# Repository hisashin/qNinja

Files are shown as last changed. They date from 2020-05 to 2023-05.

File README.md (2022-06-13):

# Open Source $300 Real Time PCR and LAMP machine "qNinja"

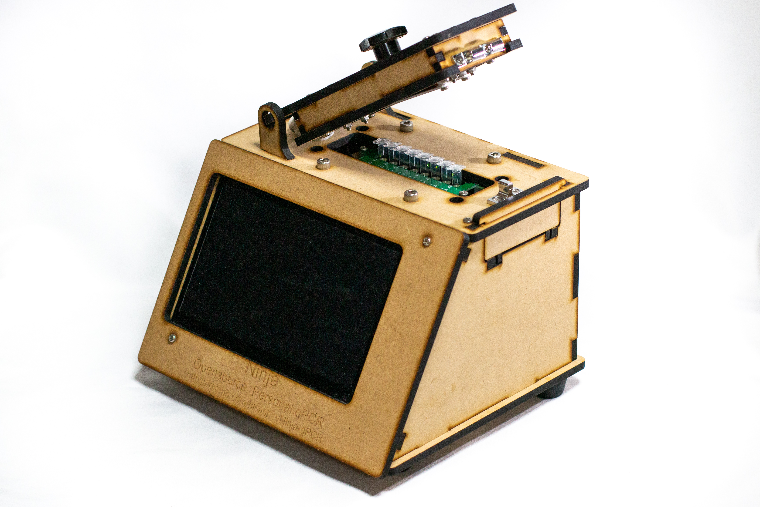
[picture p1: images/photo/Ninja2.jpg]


# $50 qLAMP machine "[qNinja Lite](https://github.com/hisashin/qNinjaLite)" is also available



## Reference Links
- [qNinja portal](https://qninja.hisa.dev)

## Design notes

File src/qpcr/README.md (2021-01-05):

# Ninja-qPCR core application

This directory contain the core application of Ninja-qPCR.

* ninjaqpcr.js : Core functionalities for running experiments and control devices. [More...](./API_ninjaqpcr.md)
* experiment_manager.js : Manager of experiment logs [More...](./API_log_manager.md)
* protocol_manager.js : Manager of experiment logs [More...](./API_protocol_manager.md)
* optics_analysis.js : Fluorescence analyzer class providing mathematical functionalities
  * Basic qPCR analysis
  * Baseline & threshold calculation (users can also set these values manually.)
  * Standard curve
  * Melt curve analysis

## Standalone demo

"demo.js" shows a demo of calling the core module. It simulates a typical qPCR + melt curve profile.

```
node demo.js
```

## Usage of NinjaQPCR class
Import the qPCR module.

```
const NinjaQPCR = require("./ninjaqpcr");
const hardwareConf = require("./conf/dummy_hardware_conf.js");
const qpcr = new NinjaQPCR(hardwareConf);

```

## Protocols

### Examples

* protocol_example.js : Typical protocol with initial hold, qPCR cycles and melt curve.
* protocol_example.js : Very short protocol for rapid testing.

### Format

```
{
  id: "2B93DB54-E14D-444F-BAEE-5B595F3FB917",
  lid_temp: 40.0,
  final_hold_temp:20.0,
  name: "Dev Protocol",
  stages: [
    {  
      type: Constants.StageType.HOLD,
      repeat: 1,
      steps: [
        { label:"hold", temp:DEMO_TEMP_HIGH, duration:5.0, data_collection:[] }
      ]
    },
    {
      type: Constants.StageType.QPCR,
      repeat: 3,
      steps: [
        { label:"denature", temp:DEMO_TEMP_HIGH, duration:6.0, data_collection:[3, 4] },
        { label:"anneal", temp:DEMO_TEMP_MEDIUM, duration:6.0, data_collection:[3, 4] },
        { label:"extend", temp:DEMO_TEMP_LOW, duration:6.0, data_collection:[3, 4] }
      ]
    },
    {
      type: Constants.StageType.MELT_CURVE,
      repeat: 1,
      steps: [
        { label:"denature", duration:5, temp:DEMO_TEMP_HIGH, data_collection:[] },
        { label:"cool", duration:5, temp:DEMO_TEMP_MEDIUM, data_collection:[] },
        { label:"melt", ramp_speed: 0.4, duration:5.0, temp:DEMO_TEMP_HIGH, data_collection:[1] }
      ]
    }
  ]
};
```

### Fields

Protocol
* id : UUID of the protocol. It corresponds the name of the file.
* lid_temp : Temperature of the head lid (in Celsius)
* final_hold_temp : Temperature of the head lid (in Celsius)
* name : Name of the protocol
* stages : List of stages (See below.)

Stage
* type : Type of the stage. 1=HOLD, 2=QPCR, 3=MELT_CURVE, 4=PCR (without fluorescence measurement)
* repeat : Number of cycles
* steps : List of steps (See below.)

Step
* label : Name
* duration : Hold duration (in secs)
* temp : Well temperature (in Celsius)
* data_collection : List of fluorescence data collection. 1=RAMP_CONTINUOUS, 2=HOLD_CONTINUOUS, 3=RAMP_END, 4=HOLD_END

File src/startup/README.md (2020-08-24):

Startup scripts

* The device is configured by /etc/rc.local to execute startup.sh.
* It checks the input value on the mode pin.
* If the mode pin's value is HIGH, it calls start_ap_mode.sh
* If the mode pin's value is LOW, it calls start_normal_mode.sh

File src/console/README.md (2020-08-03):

# Ninja qPCR Console

## Server

```
node ws_server.js
```

The server runs on localhost:2222.

The server app has WebSocket and REST interfaces. 

While the WebSocket API provides real-time device monitor and controller functionalities, the REST API is intended to manage protocols and logs. 
Exceptionally, paths beginning with "/device" return information about ongoing experiments so that a browser can show the progress just after joining it.

### REST API:

* /protocols : 
  * GET: Get list of protocols
  * POST: Add new protocol
* /protocols/{protocol_id} : 
  * GET: Get single protocol
  * PUT: Update single protocol
  * DELETE: Delete single protocol
* /logs : Get list of experiment logs
* /logs/latest : Get latest log
* /logs/{log_id} : Get single log
* /device : Get device status
* /device/experiment : Get current experiment
* /device/experiment/protocol : Get current protocol (Empty if the device is idle)
* /device/experiment/config : Get current protocol (Empty if the device is idle)
* /device/experiment/progress : Get progress of current protocol
* /device/experiment/baseline" : Get fluorescence baseline & threshold values

### WebSocket API:

#### Client to server commands
```
{
  category: <String>,
  data: <Object>
}
```

Categories

* experiment.start :  Start an experiment
* experiment.pause : Pause an ongoing experiment
* experiment.resume : Resume an paused experiment
* experiment.abort : Abort an ongoing or paused experiment
* experiment.finish : Finish the experiment. This command is accepted only when the device is at "Final hold" state after an experiment. By this command, the device stop heat units and become "Idle" again.
* experiment.registerProtocol : Register a protocol for the next experiment.

#### Server to client

```
{
  category: <String>,
  data: <Object>
}
```
* experiment.transition : Experiment-level status changes such as stages, cycles and steps.
* experiment.progress : Current progress including temperatures, stages and steps. The latest data can also be obtained by /device/progress of the REST API.
* experiment.fluorescence : Results of fluorescence measurements.
* experiment.fluorescenceEvent : Significant events related to fluorescence measurements, such as 
  * Start and end of continuous measurement
  * Notification of baseline and threshold determination.
* experiment.start
* experiment.finish
* device.transition : Notify device-level (not experiment-level) status change
* (TODO) device.error : Notify device-level errors

Each category corresponds to event handlers of NinjaQPCR class:

| Category | Function |
| ---- | --- |
| experiment.transition | onThermalTransition |
| experiment.progress | onProgress |
| experiment.fluorescence | onFluorescenceDataUpdate |
| experiment.fluorescenceEvent | onFluorescenceEvent |
| experiment.start | onStart |
| experiment.finish | onComplete |
| device.transition | onDeviceStateChange |
| device.error | onError |

For details of data format, see [the document of NinjaQPCR class](../qpcr/API_ninjaqpcr.md).

# Client

The client is implemented as a Vue.js app.

Run (and hot reload):
```
npm run serve
```
By default, the app runs on
- Local:   http://localhost:8080 
- Network: http://192.168.1.15:8080

Build for production:
```
npm run build
```

Static files (HTML, css and js) are saved to "dist" directory.

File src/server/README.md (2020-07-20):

# Ninja-qPCR server

The endpoint for the console that controls the instrument.

It should handle the following functions:

* Start, pause and experiment experiments (experiment protocol)
* Return current status of the thermal cycler
* Return fluorescence data
* Notify thermal cycler's transition events (stages and steps)
* Notify errors and alerts

## Development
```
yarn
yarn start
```

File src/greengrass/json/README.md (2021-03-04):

# Test your POST_URL

```
curl -X POST -H "Content-Type: application/json" -d @src/greengrass/json/qPCR-protocol-sample.json (POST_URL)
curl -X POST -H "Content-Type: application/json" -d @src/greengrass/json/qPCR-log-sample.json (POST_URL)
```

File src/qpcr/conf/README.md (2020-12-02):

This directory contain hardware config files.

* hardware.json : Top config including well layout, model specifications.
* ninjaqpcr_*.js : Board-specific files. Some files are intended to run only with some parts of the device or only simulator.

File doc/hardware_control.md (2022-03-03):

# Fluorescence measurement

## Sequence

1. Activate LED
    * Set potentiometer value
    * Select LED channel
2. Select photodiode MUX channel
    * Select MUX
    * Select channel
3. Read ADC value 
    * Wait until the ADC value becomes stable
    * Read ADC value

This sequence is performed for each channel.

# Wiring

* All I2C devices on the board share SDA and SCL wires.
* Device addresses
    * Potentiometer (For LED control) : 0x2F
    * LED driver : 0x05
    * ADC : 0x40
* Photodiodes
    * Wells and MUX channels association
        * North (Ch 0) (Well 1 - Well 8) 7,5,3,1,15,13,11,9
        * North (Ch 1) (Well 1 - Well 8) 6,4,2,0,14,12,10,8
        * South (Ch 0) (Well 9 - Well 16) 8,10,12,14,0,2,4,6
        * South (Ch 1) (Well 9 - Well 16) 9,11,13,15,1,3,5,7
* LED and driver channels association
    * North (Well 1 - Well 8) 11,10,9,8,12,13,14,15,
    * South (Well 9 - Well 16) 4,5,6,7,3,2,1,0
    
# Pseudo code

## Setup
```

pin_mux_select = ...
pin_mux_s0 = ...
pin_mux_s1 = ...
pin_mux_s2 = ...
pin_mux_s3 = ...

well_to_led_ch = [
    11,10,9,8,12,13,14,15,
    4,5,6,7,3,2,1,0
]

well_to_mux_ch = [
    [ 
        7,5,3,1,15,13,11,9, #  North
        8,10,12,14,0,2,4,6 # South
    ], # Optical channnel 0
    [
        6,4,2,0,14,12,10,8, #  North
        9,11,13,15,1,3,5,7 # South
    ] # Optical channnel 1
]

func setup () : 
    init_i2c_bus()
    led_driver_init()
    adc_init()
```

## Measure all Wells

```
for well in 0..15 :
    for optical_channel in 0..1 :
        fluo = read_fluo (well, optical_channel)

func read_fluo (well, optical_channel) :

    led_channel = well_to_led_ch[well]
    mux = (int) well / 8  # 0=>North, 1=>South
    mux_channel = well_to_mux_ch[optical_channel][well]

    set_potentiometer_wiper (pot_wiper)
    select_led_channel (led_channel)
    gpio_write (pin_mux_select, mux)
    select_mux_channel (mux_channel)
    adc_select_channel () # AIN3->P, AIN2->N
    delay_msec (2)
    fluo_raw = adc_read_conversion ()
    return calc_fluo (fluo_raw, pot_wiper)
```

## MUX
```
func select_mux_channel (channel) :
    gpio_write (pin_mux_s0, 0x01&(ch>>0) )
    gpio_write (pin_mux_s1, 0x01&(ch>>1) )
    gpio_write (pin_mux_s2, 0x01&(ch>>2) )
    gpio_write (pin_mux_s3, 0x01&(ch>>3) )

```
## LED driver
```
i2c_addr_led_driver = 0x05
REG_ADDR_LEDOUT0 = 0x02

func led_driver_init () :
    # Set blank control mode
    i2c_write(i2c_addr_led_driver, [0x00, 0b10001001] )

    first_val = 0x18 | (0b01 << 7)
    vals = [first_val]
    for 0..16
        vals.append(0xFF)
    # Send 17 bytes (address + 0xFF x 16)
    i2c_write(i2c_addr_led_driver, vals)

func select_led_channel (channel) :
    leds = [...]
    for i in 0..15
        leds[i] = (i == channel) ? 1 : 0

    vals = []

    # 4 bytes for 16 channels
    for group in 0..3
        # 2 bits for each channel
        val = 0b00000000
        for i in 0..3
            mode = leds[group * 4 + i]
            val = val | (mode << (i*2))
        vals[group] = val

    addr_byte = REG_ADDR_LEDOUT0 | (0b01 << 7)

    # Send 5 bytes (address + LED values)
    reg_values = [addr_byte] + [vals] 
    i2c_write(i2c_addr_led_driver, reg_values)

```
## Potentiometer
```
i2c_addr_pot = 0x2F

func set_potentiometer_wiper (wiper) : 
    val0 = wiper >> 8 & 0x01
    val1 = wiper & 0xFF
    i2c_write(i2c_addr_pot, [val0, val1]);

```

## ADC

```
i2c_addr_adc = 0x40

COMMAND_RDATA = 0x10
COMMAND_RREG = 0b00100000 # 0010 rrxx : Read register at address rr
COMMAND_WREG = 0b01000000
COMMAND_SSYNC = 0b00001000

func adc_write_reg (reg_address, value) :
    command = COMMAND_WREG | (0b11&reg_address) << 2;
    i2c_write(i2c_addr_adc, [command, value])
    i2c_send(i2c_addr_adc, COMMAND_SSYNC)

func adc_read_reg (address) :
    command = COMMAND_RREG | (0b11&addr) << 2;
    i2c_send(i2c_addr_adc, command)
    return i2c_receive(i2c_addr_adc)

func adc_init () :
    data_rate_600sps = 0b101
    current_conf_val = adc_read_reg(0x01);
    new_conf_val = (0b00011111 & current_conf_val) | (data_rate_600sps << 5)
    adc_write_reg(0x01, new_conf_val)

func adc_select_channel () :
    mux_bits = 0b0111 # AIN3->P, AIN2->N
    current_val = adc_read_reg(0x00)
    new_val = (0b00001111 & current_val) | (mux_bits << 4);
    adc_write_reg(0x00, new_val);

func adc_read_conversion () : 
    i2c_send(i2c_addr_adc, COMMAND_RDATA)

    # Read 3 bytes
    val = i2c_receive(i2c_addr_adc)
    val <<= 8;
    val |= i2c_receive(i2c_addr_adc)
    val <<= 8;
    val |= i2c_receive(i2c_addr_adc)

    if (val & 0x00800000)
      val = ~val + 1;
      val = -(val & 0xFFFFFF)
    return val / (1.0 * 0x00800000)

func calc_fluo (fluo_raw, pot_wiper) :
    # TODO

```

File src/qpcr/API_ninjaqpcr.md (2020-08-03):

# class NinjaQPCR

## constructor (hardwareConf)

## Public functions

### setEventReceiver (receiver)

Set an object to receive events.

### start (protocol)

### pause ()

### resume ()

### abort ()

### finish ()

## Event handling

You can get notified of events by setting a receiver object.

```
qpcr.setEventReceiver(receiver)
```

Functions below are defined. All of them are optional.
  
### onProgress(data)

Tells current progress of the experiment every 0.5 second.

```
{ 
  well: 50,
  lid: 40,
  state: 
  { 
    state: 'ramp', 
    stage: 0,
    repeat: 0,  
    step: 0, 
    stepElapsed: 5025 
  },
  remaining: 153475,
  elapsed: 8045 
}
```

* well (float) : Temperature of the well block
* lid (float) : Temperature of the heat lid
* remaining (long int) : Estimated remaining time in milliseconds
* elapsed (long int) : Elapsed time in milliseconds
* state (object) : State of the experiment
  * state (string) : Label of the state. (preheat/ramp/hold/complete)
  * stage (int) (*) : Index of the stage. 
  * repeat (int) (*) : Index of the cycle
  * step (int) (*) : Index of the step
  * stepElapsed (long) (*) : Elapsed time of the step in milliseconds
  
Fields with "(*)" are empty when the state is "preheat" or "compete".

### onThermalTransition(transition)

Notifies state changes of the thermal cycler.

```
{ 
  from:
   { state: 'hold', stage: 1, step: 0, repeat: 0, stepElapsed: 5028 },
  to:
   { state: 'ramp', stage: 1, step: 0, repeat: 0, stepElapsed: 0 } }
}
```

* from (object) : Previous state.
* to (object) : Current state.

### onError(error)

Notifies device errors.
  
### onStart(data)

Notifies that the experiment started.

```
{ 
  id: '34aa55dc-e63d-4562-836d-6900dee11608',
  protocol: '2B93DB54-E14D-444F-BAEE-5B595F3FB917' 
}
```
  
### onComplete(data)

Tell the end of the experiment. The well unit is still working to keep the final hold temperature.
"Finish" command is needed to completely stop heat units and make the device ready again.

```
{ 
  id: '34aa55dc-e63d-4562-836d-6900dee11608',
  protocol: '2B93DB54-E14D-444F-BAEE-5B595F3FB917' 
}
```
  
### onDeviceStateChange(data)
  
### onFluorescenceDataUpdate(data)

Tell result of fluorescence measurement.

```
[ 0.10801242489714052,
  0.12294936026411177,
  0.11420738944199534,
  0.13175764679533242,
  0.12903787941280465,
  0.10887617636084554,
  0.13071267983725746,
  0.12279237404504303 ]
```
  
### onFluorescenceEvent (data)

```
{ type: 'measure' }
```

* type (string) : Type of the event

Event types are

* measure : One-shot measurement (at ends of steps of qPCR stages)
* start : Starting continuous measurement (for baseline or melt curve)
* stop : Stopping continuous measurement
* baseline : End of baseline measurement. At this time, thresholds are determined automatically.

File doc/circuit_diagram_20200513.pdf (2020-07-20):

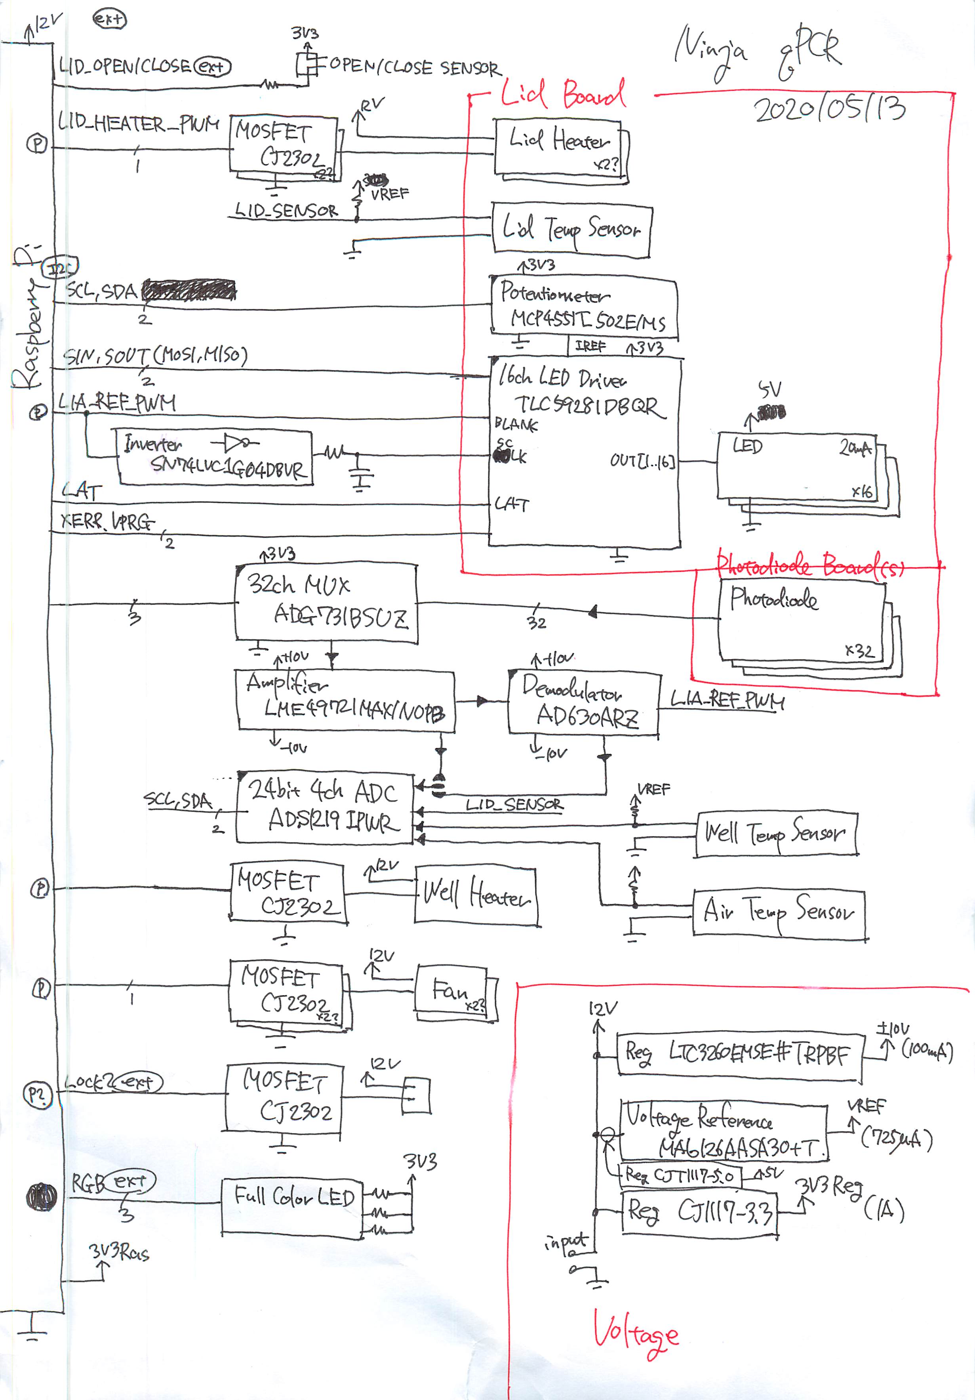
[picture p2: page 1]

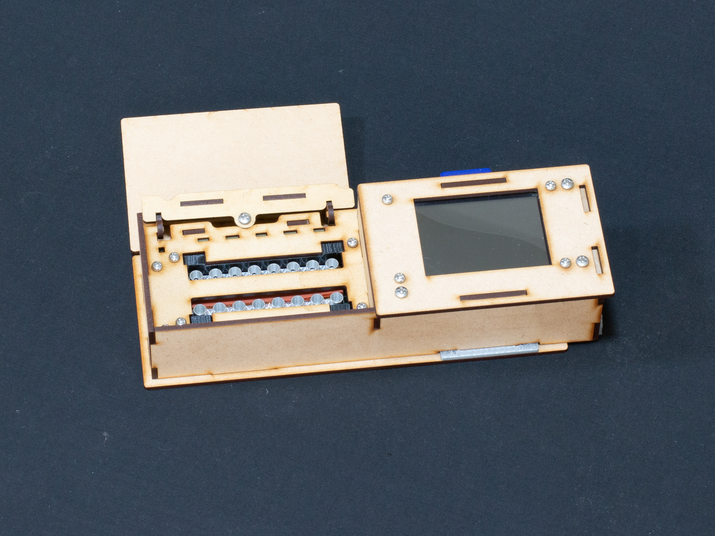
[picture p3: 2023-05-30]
images/photo/qlite_mdf_open_1.jpg

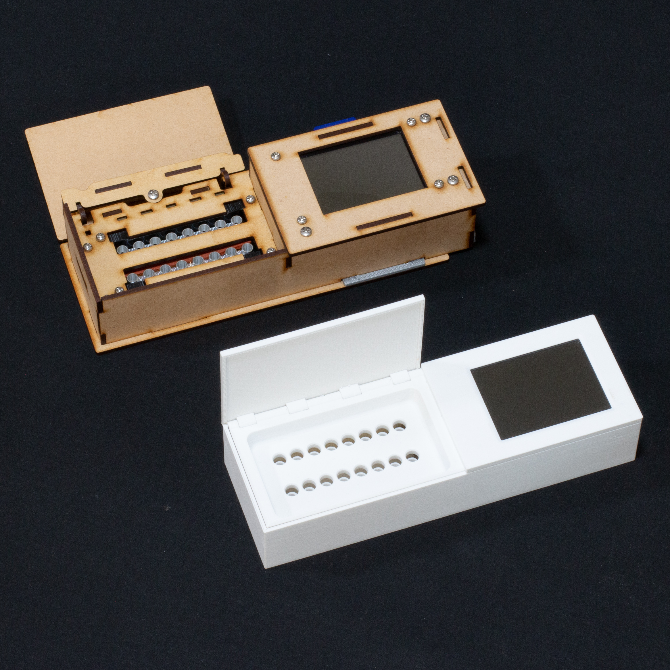
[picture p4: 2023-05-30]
images/photo/20230530/v_IMG_2483.jpg

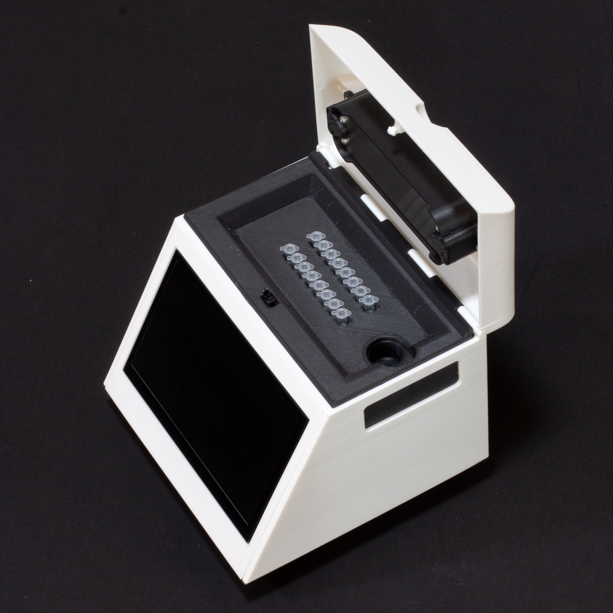
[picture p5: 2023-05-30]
images/photo/q_3dp_open_3.jpg

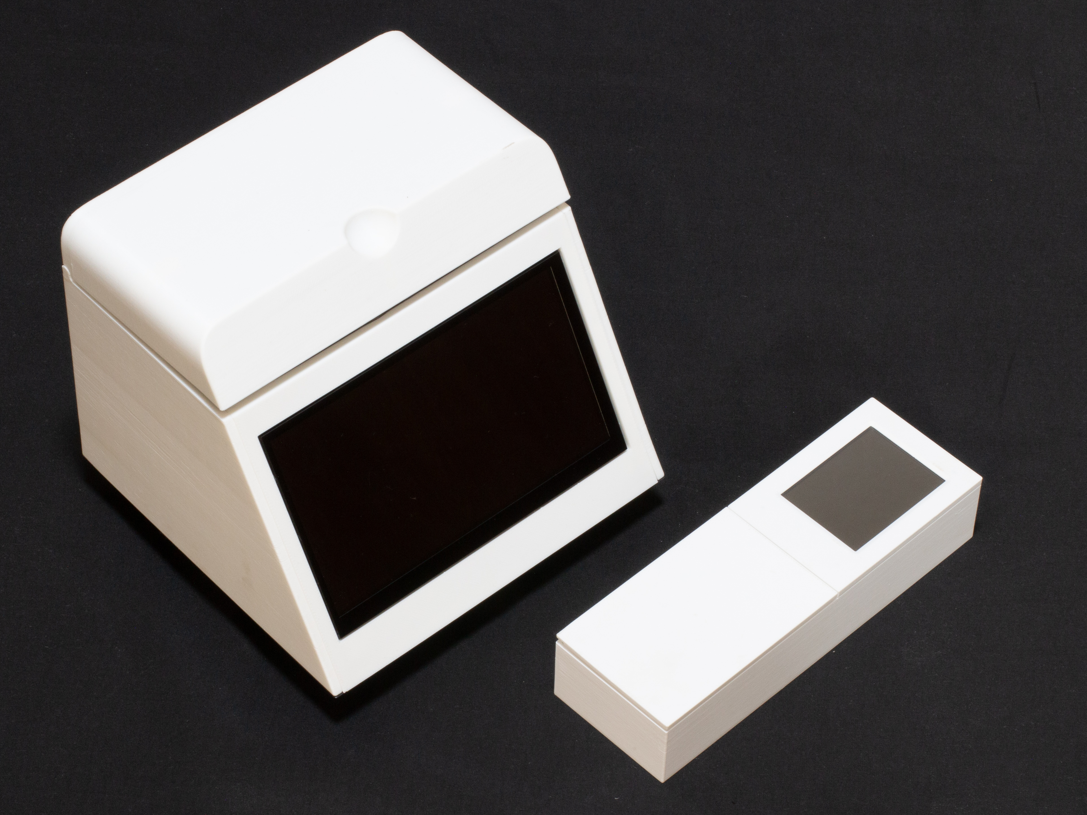
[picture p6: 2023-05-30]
images/photo/q_qlite_3dp_close_1.jpg

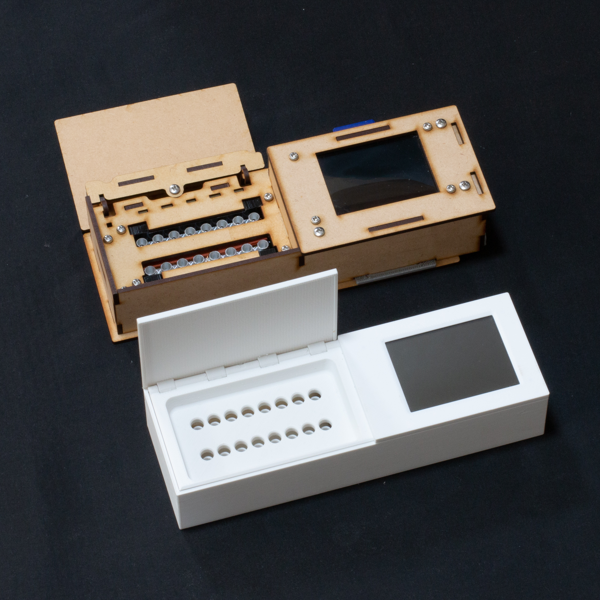
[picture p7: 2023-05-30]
images/photo/20230530/v_IMG_2487.jpg

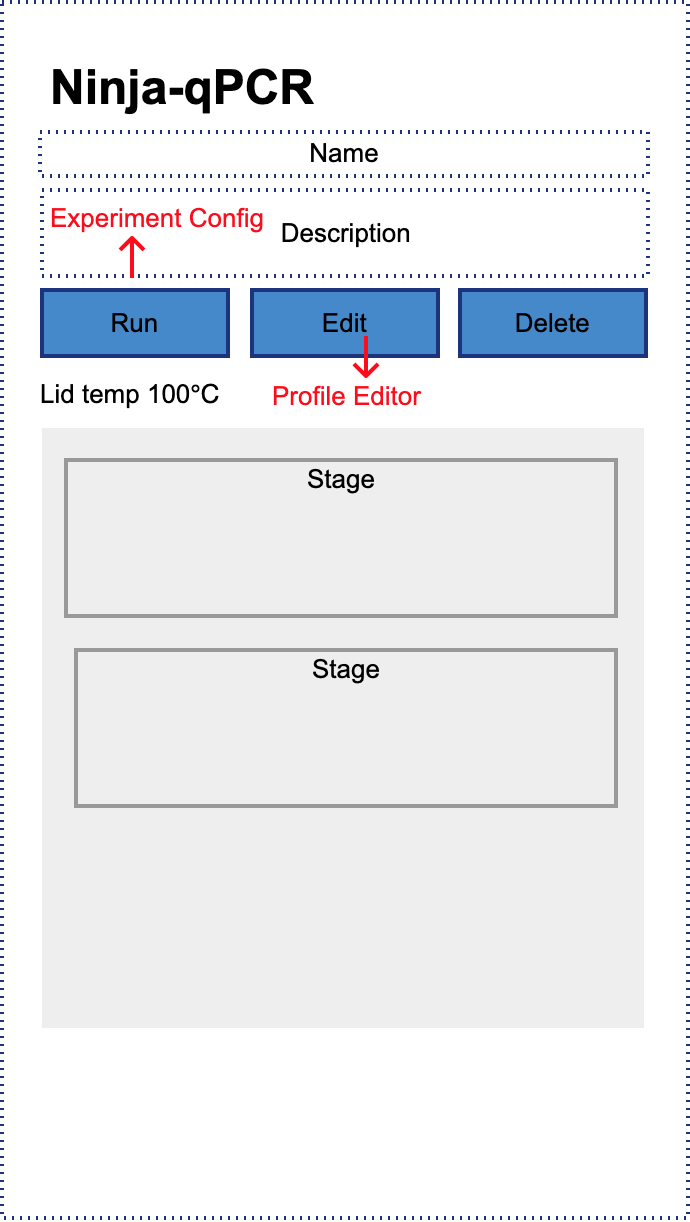
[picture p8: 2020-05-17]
src/docs/mockup/pages/profile_detail.png

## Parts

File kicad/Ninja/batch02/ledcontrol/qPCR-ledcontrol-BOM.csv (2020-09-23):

Id | Designator | Package | Quantity | Designation | Supplier and ref
1 | JP1 | SolderJumper-3_P2.0mm_Open_TrianglePad1.0x1.5mm | 1 | Jumper_3_Open
2 | N_CONN1,S_CONN1,U1 | Con_2x05 | 3 | Conn_02x05
3 | U2 | SN74LVC1G04DBVR | 1 | SN74LVC1G04DBVR
4 | U3 | MCP4551T-502E&slash_MS | 1 | MCP4551T-502E_MS
5 | U4 | TLC59281DBQR | 1 | TLC59281DBQR
6 | C1,C2 | C_0805_HandSoldering | 2 | C

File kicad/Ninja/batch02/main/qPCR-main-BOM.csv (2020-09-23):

Id | Designator | Package | Quantity | Designation | Supplier and ref
1 | J1 | Raspberry_Pi_3A+_Socketed_THT_FaceDown_MountingHoles_minimum | 1 | Raspberry_Pi_3A_Plus_wpi
2 | R16,R14,R15,R17,R18,R19,R20 | R_0603_HandSoldering | 7 | R
3 | BODY1,LED,LID | Con_2x05 | 3 | Conn_02x05
4 | C1,C2,C4,C16,C27 | CP_Elec_6.3x5.8 | 5 | 100uF
5 | C3,C5,C6,C22,C28,C33,C34,C35 | C_0805_HandSoldering | 8 | 22uF
6 | C7,C8,C10,C21,C31,C36 | C_0805_HandSoldering | 6 | 10uF
7 | C9,C11,C13,C25,C29,C32,C37,C38 | C_0805_HandSoldering | 8 | 0.1uF
8 | C12,C14,C15,C18,C19,C26 | C_0603_HandSoldering | 6 | 0.01uF
9 | C17 | C_Disc_D5.0mm_W2.5mm_P5.00mm | 1 | 3300pF
10 | C20,C24 | C_0805_HandSoldering | 2 | 1uF
11 | C23 | C_0603_HandSoldering | 1 | 820pF
12 | C30 | C_0603_HandSoldering | 1 | (5-100pF)
13 | J2,J10,J11 | Pin_Header_Straight_1x03_Pitch2.54mm | 3 | Conn_01x03_Male
14 | GPIO7,GPIO25 | Pin_Header_Straight_1x01_Pitch2.54mm | 2 | Conn_01x01_Male
15 | J5,J6,J7 | Pin_Header_Straight_2x03_Pitch2.54mm | 3 | Conn_02x03_Odd_Even
16 | J8 | BarrelJack_Horizontal | 1 | Barrel_Jack_Switch
17 | J9 | Molex_MiniFit-JR-5556-24A_2x12x4.20mm_Straight | 1 | ATX-24
18 | J_12V1 | Pin_Header_Straight_1x02_Pitch2.54mm | 1 | Conn_01x02_Male
19 | L1 | IND_VLS5045EX-4R7M | 1 | 3.3uH(ALPS GLMC / TDK SPM6530)
20 | PHOTOSENSING | Pin_Header_Straight_1x14_Pitch2.54mm | 1 | Conn_01x14_Male
21 | Q1,Q2,Q3,Q4,Q5,Q6 | SOT95P240X112-3N | 6 | Q_NMOS_GSD
22 | R1,R2,R3,R8,R9,R10 | R_0603_HandSoldering | 6 | 1k
23 | R4,R5,R6,R7,R11,R12,R13 | R_0603_HandSoldering | 7 | 10k
24 | R22,R27 | R_0603_HandSoldering | 2 | 22X
25 | R23,R28 | R_0603_HandSoldering | 2 | 3X
26 | R24 | R_0603_HandSoldering | 1 | 120k
27 | R25 | R_0603_HandSoldering | 1 | 1.8k/0
28 | R26 | R_0603_HandSoldering | 1 | 22k
29 | U1 | DN4_PWR | 1 | DIN4_PWR
30 | U2 | SOIC-8-1EP_3.9x4.9mm_Pitch1.27mm | 1 | IFX1763
31 | U3 | SOIC-8-1EP_3.9x4.9mm_Pitch1.27mm | 1 | BD9D320EFJ-E2
32 | U4 | LTC3260EMSE-TRPBF | 1 | LTC3260EMSE-TRPBF
33 | U5 | SOT-223 | 1 | CJT1117-3.3
34 | U6 | SN74LVC1G04DBVR | 1 | SN74LVC1G04DBVR
35 | U7 | SN74LVC2G66DCUR | 1 | SN74LVC2G66DCUR
36 | R21 | R_0603_HandSoldering | 1 | 100K
37 | SW1 | SW_TH_Tactile_Omron_B3F-10xx | 1 | TACTILE_4

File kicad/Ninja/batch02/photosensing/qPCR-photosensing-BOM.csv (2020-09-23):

Id | Designator | Package | Quantity | Designation | Supplier and ref
1 | C1,C3,C7,C9 | R_0603_HandSoldering | 4 | 0.1uF
2 | C8,C6 | R_1206_HandSoldering | 2 | 0.47uF
3 | J3,J4 | Pin_Header_Straight_1x05_Pitch2.54mm | 2 | Conn_01x05_Male
4 | R1 | R_0603_HandSoldering | 1 | 1k
5 | R2 | R_0603_HandSoldering | 1 | 6.2k
6 | R3,R4 | R_0603_HandSoldering | 2 | 10k
7 | R5 | R_0603_HandSoldering | 1 | 1800
8 | R6 | R_0603_HandSoldering | 1 | 1.1M
9 | R7,R8 | R_0603_HandSoldering | 2 | 560
10 | U1 | AD630ARZ | 1 | AD630ARZ
11 | U2 | ADS1219IPWR | 1 | ADS1219IPWR
12 | U3 | LME49721MAX&slash_NOPB | 1 | LME49721MAX_NOPB
13 | C2,C4,C5 | C_0805_HandSoldering | 3 | C
14 | C10 | C_Disc_D3.0mm_W2.0mm_P2.50mm | 1 | 10pF
15 | C11,C12 | R_1206_HandSoldering | 2 | 0.22uF
16 | J1 | Pin_Header_Angled_1x14_Pitch2.54mm | 1 | Conn_01x14_Male
17 | J2 | Pin_Header_Straight_1x02_Pitch2.54mm | 1 | Conn_01x02_Male

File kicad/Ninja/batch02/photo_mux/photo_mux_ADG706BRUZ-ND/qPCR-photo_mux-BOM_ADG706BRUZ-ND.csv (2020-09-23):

Id | Designator | Package | Quantity | Designation | Supplier and ref
1 | C1,C2 | C_0603_HandSoldering | 2 | C
2 | J1,J2 | Pin_Header_Straight_1x05_Pitch2.54mm | 2 | Conn_01x05_Male
3 | JP1,JP2,JP3 | SolderJumper-3_P2.0mm_Open_TrianglePad1.0x1.5mm | 3 | Jumper_3_Open
4 | N_PD1,N_PD2,S_PD1,S_PD2 | Con_2x05 | 4 | Conn_02x05
5 | R1,R2,R3,R4,R5,R6 | R_0603_HandSoldering | 6 | R
6 | U1,U4 | ADG706BRUZ | 2 | ADG706BRUZ
7 | U3 | SN74LVC1G04DBVR | 1 | SN74LVC1G04DBVR

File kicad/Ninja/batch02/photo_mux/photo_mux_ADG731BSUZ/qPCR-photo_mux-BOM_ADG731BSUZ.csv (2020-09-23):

Id | Designator | Package | Quantity | Designation | Supplier and ref
1 | C1,C2 | C_0805_HandSoldering | 2 | C
2 | J1,J2 | Pin_Header_Straight_1x05_Pitch2.54mm | 2 | Conn_01x05_Male
3 | JP1,JP2 | SolderJumper-3_P2.0mm_Open_TrianglePad1.0x1.5mm | 2 | Jumper_3_Open
4 | N_PD1,N_PD2,S_PD1,S_PD2 | Con_2x05 | 4 | Conn_02x05
5 | R1,R2,R3,R4,R5,R6 | R_0603_HandSoldering | 6 | R
6 | U1 | ADG731BSUZ | 1 | ADG731BSUZ

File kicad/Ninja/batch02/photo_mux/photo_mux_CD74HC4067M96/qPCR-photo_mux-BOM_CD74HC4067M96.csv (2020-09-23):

Id | Designator | Package | Quantity | Designation | Supplier and ref
1 | J1,J2 | Pin_Header_Straight_1x05_Pitch2.54mm | 2 | Conn_01x05_Male
2 | JP1 | SolderJumper-3_P2.0mm_Open_TrianglePad1.0x1.5mm | 1 | Jumper_3_Open
3 | N_PD1,N_PD2,S_PD1,S_PD2 | Con_2x05 | 4 | Conn_02x05
4 | U1,U3 | CD74HC4067M96 | 2 | CD74HC4067M96
5 | U2 | SN74LVC1G04DBVR | 1 | SN74LVC1G04DBVR

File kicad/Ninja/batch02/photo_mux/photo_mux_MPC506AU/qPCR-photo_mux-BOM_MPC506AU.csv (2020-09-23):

Id | Designator | Package | Quantity | Designation | Supplier and ref
1 | C1,C2,C3,C4 | C_0805_HandSoldering | 4 | C
2 | J1,J2 | Pin_Header_Straight_1x05_Pitch2.54mm | 2 | Conn_01x05_Male
3 | JP1 | SolderJumper-3_P2.0mm_Open_TrianglePad1.0x1.5mm | 1 | Jumper_3_Open
4 | N_PD1,N_PD2,S_PD1,S_PD2 | Con_2x05 | 4 | Conn_02x05
5 | U1,U3 | MPC506AU | 2 | MPC506AU
6 | U2 | SN74LVC1G04DBVR | 1 | SN74LVC1G04DBVR

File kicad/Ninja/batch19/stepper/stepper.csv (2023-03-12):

Id | Designator | Footprint | Quantity | Designation | Supplier and ref
1 | J2 | PinHeader_1x05_P2.54mm_Vertical | 1 | Conn_01x05_Male
2 | J3 | PinHeader_1x02_P2.54mm_Vertical | 1 | Conn_01x02_Male
3 | J1 | PinHeader_1x04_P2.54mm_Vertical | 1 | Conn_01x04_Male
4 | C4 | C_0805_2012Metric | 1 | 10uF
5 | RSENB1,RSENA1 | R_0603_1608Metric | 2 | R
6 | J4 | BarrelJack_Horizontal | 1 | Barrel_Jack_Switch
7 | U1 | TSSOP-16-1EP_4.4x5mm_P0.65mm_EP3x3mm_ThermalVias | 1 | MP6507GF-Z
8 | C2 | C_0603_1608Metric | 1 | 0.1uF
9 | C5 | C_0603_1608Metric | 1 | 0.1uF(Low ESR ceramic)
10 | C1 | C_0805_2012Metric | 1 | 4.7uF
11 | C3 | 35TZV100M6.3X8 | 1 | 100uF

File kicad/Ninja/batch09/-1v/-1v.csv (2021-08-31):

Id | Designator | Package | Quantity | Designation | Supplier and ref
1 | C1,C6,C7 | C_0805_2012Metric_Pad1.18x1.45mm_HandSolder | 3 | 22uF
2 | C2 | C_0603_1608Metric_Pad1.08x0.95mm_HandSolder | 1 | 1uF
3 | C3 | C_0603_1608Metric_Pad1.08x0.95mm_HandSolder | 1 | 2.2uF
4 | C4 | C_0603_1608Metric_Pad1.08x0.95mm_HandSolder | 1 | 220nF
5 | C5 | C_0805_2012Metric_Pad1.18x1.45mm_HandSolder | 1 | 10uF
6 | J1 | Pin_Header_Straight_1x03_Pitch2.54mm | 1 | Conn_01x03_Female
7 | L1 | SRN6045TA-3R3Y | 1 | 22uH
8 | R1 | R_0603_1608Metric_Pad0.98x0.95mm_HandSolder | 1 | 51.1k
9 | R2 | R_0603_1608Metric_Pad0.98x0.95mm_HandSolder | 1 | 180k
10 | U1 | TPS63710DRRR | 1 | TPS63710DRRR

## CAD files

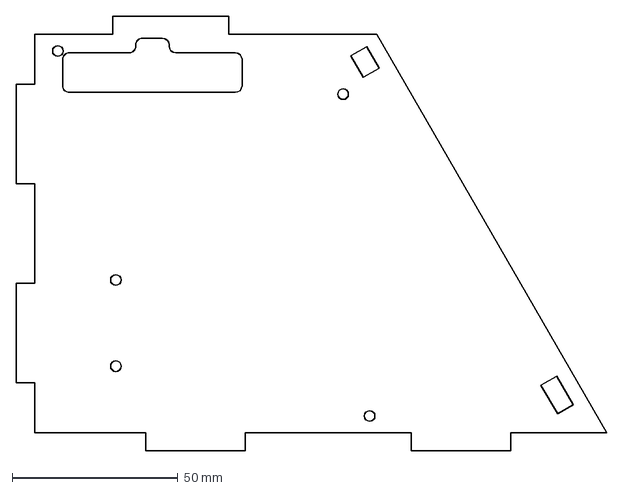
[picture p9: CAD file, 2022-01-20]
cad/2d/dxf-ver1.4/common/wood_body_left.dxf
177.9 x 131.0 mm

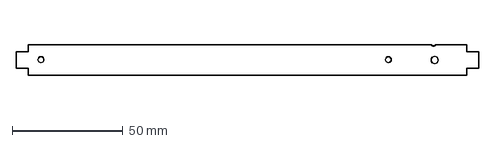
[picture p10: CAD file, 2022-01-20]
cad/2d/dxf-ver1.4/jlt-7inch/wood_lcd_holder_jtl-7inch-north.dxf
209.0 x 13.8 mm

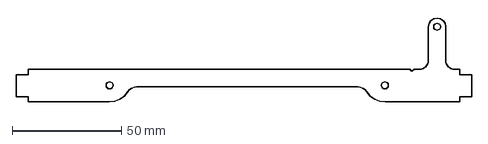
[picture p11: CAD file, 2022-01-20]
cad/2d/dxf-ver1.4/raspi/wood_lcd_holder_raspi_north.dxf
209.0 x 38.5 mm

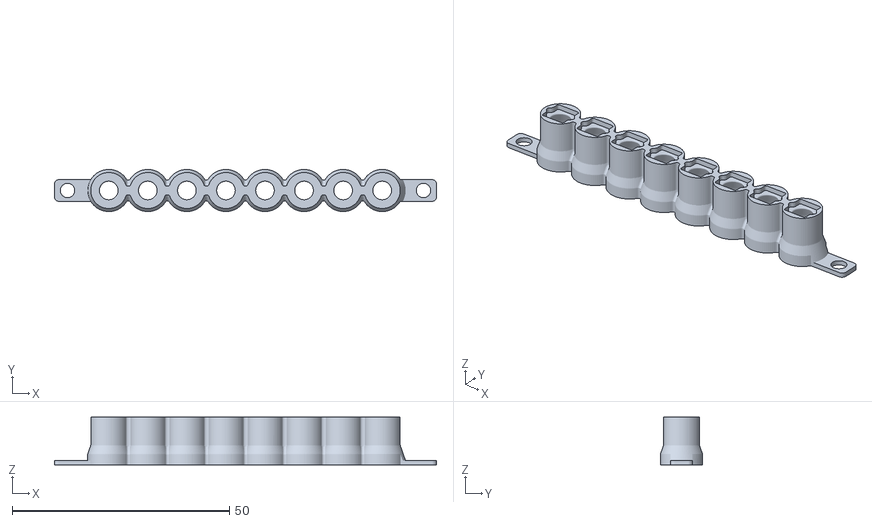
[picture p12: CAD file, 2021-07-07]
cad/3d/3dprint/led_coverA_x2.stl
88.0 x 9.70 x 11.0

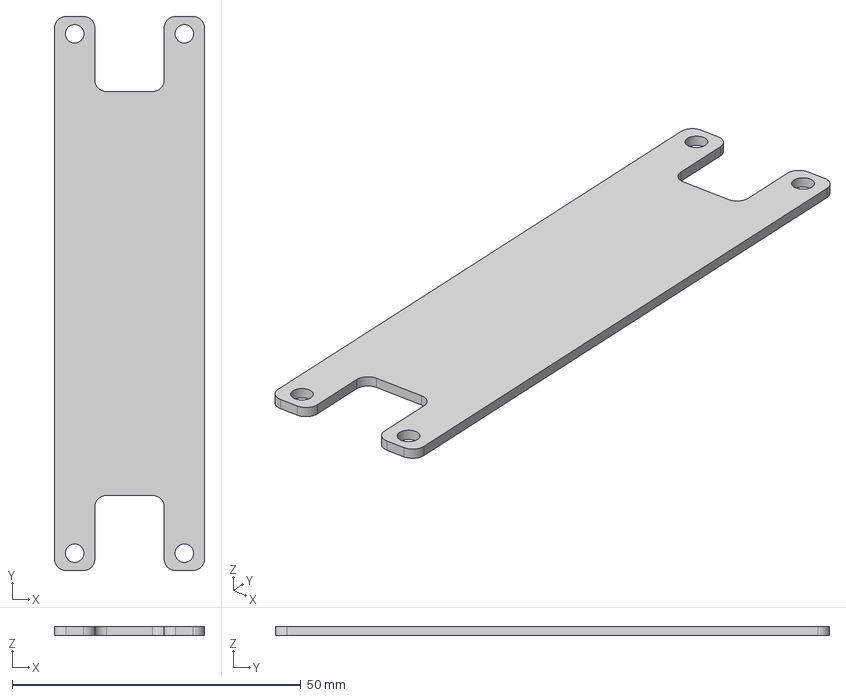
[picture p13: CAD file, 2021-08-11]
cad/3d/aluminium/lid_heating.step
26.0 x 96.0 x 1.50 mm

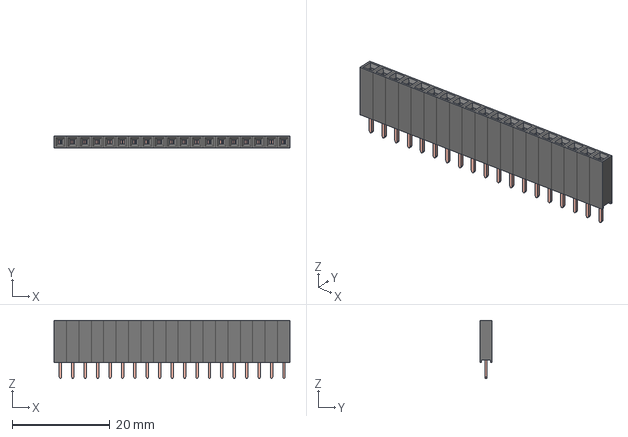
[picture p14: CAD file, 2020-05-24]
cad/3d/pcb/female_header/hf_1x19.step
48.3 x 2.48 x 11.9 mm

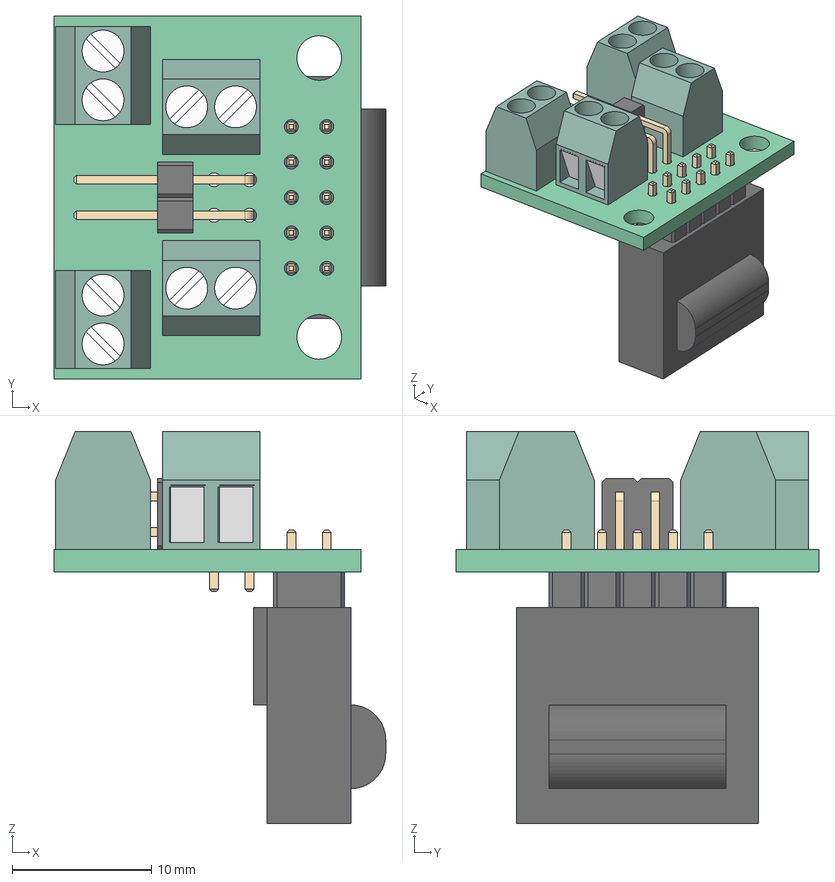
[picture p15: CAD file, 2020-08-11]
kicad/Ninja/batch01/con_body/con_body.step
23.8 x 26.0 x 28.1 mm
Local_CS_f8fe
Pcb_f8fe
PCB_Sketch_f8fe
F1_TerminalBlock_SeeedOPL320110028_v2_5F2B8A74
F2_TerminalBlock_SeeedOPL320110028_v2_5F2B8A7F
H1_TerminalBlock_SeeedOPL320110028_v2_5F2B8A8A
H2_TerminalBlock_SeeedOPL320110028_v2_5F2B8A95
J1_PinHeader_2x02_P254mm_Horizontal_5F2B93AC[2]
U1_aitendo-MIL-2x5-cable-edge_v1_5F2B8B1B[2]

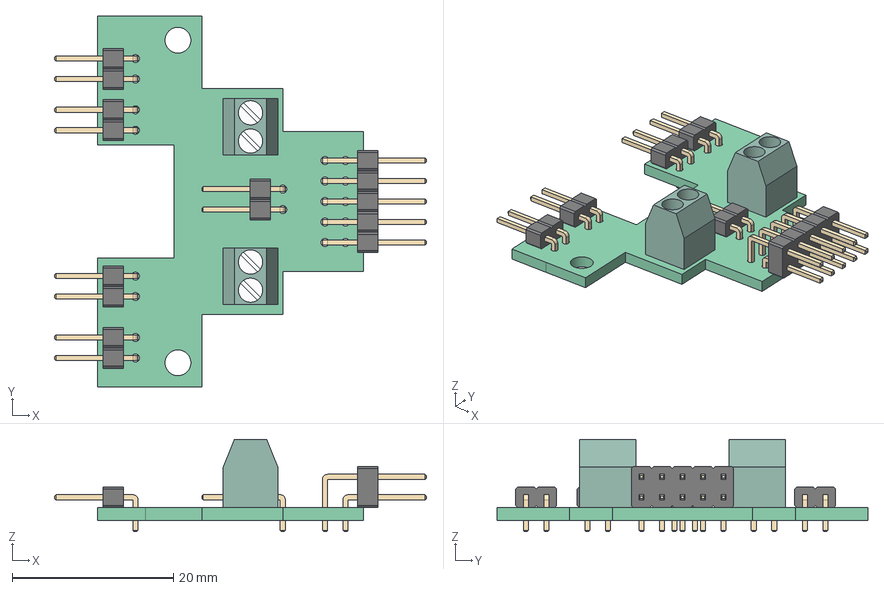
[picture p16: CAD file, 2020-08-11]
kicad/Ninja/batch01/con_lid_1x8/con_lid_1x8.step
46.1 x 46.0 x 11.5 mm
Local_CS_f5b8
Pcb_f5b8
PCB_Sketch_f5b8
T1_PinHeader_1x02_P254mm_Horizontal_5F2B81B9[2]
T2_PinHeader_1x02_P254mm_Horizontal_5F2B824F[2]
T3_PinHeader_1x02_P254mm_Horizontal_5F2B82E5[2]
T4_PinHeader_1x02_P254mm_Horizontal_5F2B8CCA[2]
U1_PinHeader_2x05_P254mm_Horizontal_5F2B5BE4[2]
He_TerminalBlock_SeeedOPL320110028_v2_5F2B8F51
H2_TerminalBlock_SeeedOPL320110028_v2_5F2B8F5B
TAIR1_PinHeader_1x02_P254mm_Horizontal_5F2B8F65[2]

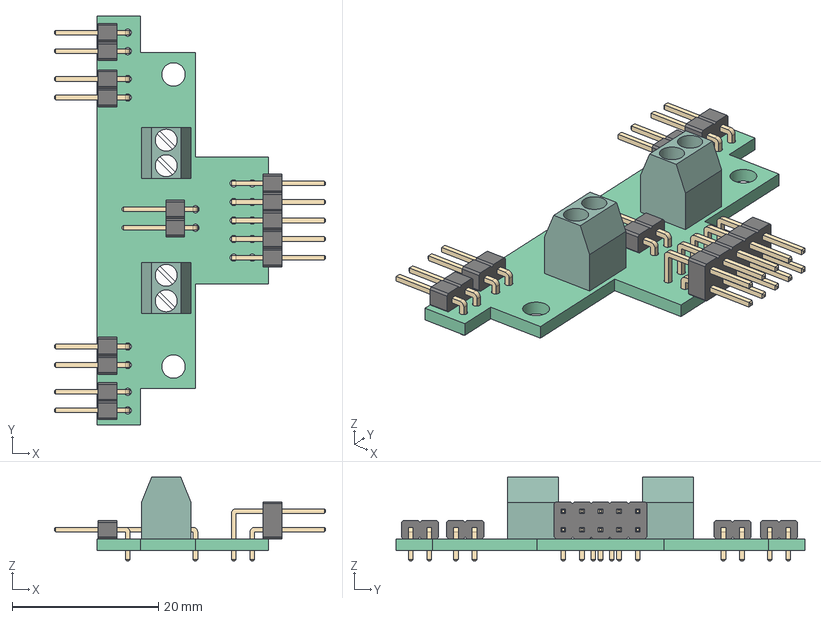
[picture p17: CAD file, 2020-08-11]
kicad/Ninja/batch01/con_lid_2x8/con_lid_2x8.step
37.1 x 56.0 x 11.5 mm
Local_CS_48ed
Pcb_48ed
PCB_Sketch_48ed
T1_PinHeader_1x02_P254mm_Horizontal_5F2B81B9[2]
T2_PinHeader_1x02_P254mm_Horizontal_5F2B824F[2]
T3_PinHeader_1x02_P254mm_Horizontal_5F2B82E5[2]
T4_PinHeader_1x02_P254mm_Horizontal_5F2CB3DF[2]
U1_PinHeader_2x05_P254mm_Horizontal_5F2B5BE4[2]
He_TerminalBlock_SeeedOPL320110028_v2_5F2B8F51
H2_TerminalBlock_SeeedOPL320110028_v2_5F2B8F5B
TAIR1_PinHeader_1x02_P254mm_Horizontal_5F2B8F65[2]

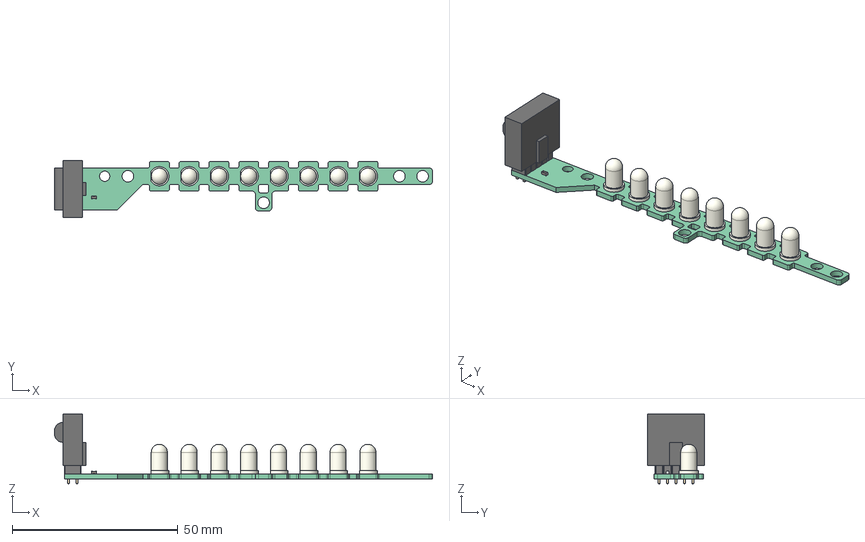
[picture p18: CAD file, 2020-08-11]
kicad/Ninja/batch01/ledarray_1x8/qPCR-ledarray_1x8.step
114.2 x 17.3 x 21.0 mm
Local_CS_7705
Pcb_7705
PCB_Sketch_7705
D1_OVLEW1CB9/OVLGC0C6B9_v3_5EFF066C[2]
D2_OVLEW1CB9/OVLGC0C6B9_v3_5EFF0639[2]
D3_OVLEW1CB9/OVLGC0C6B9_v3_5EFF0606[2]
D4_OVLEW1CB9/OVLGC0C6B9_v3_5EFF05D3[2]
D5_OVLEW1CB9/OVLGC0C6B9_v3_5EFFA656[2]
D6_OVLEW1CB9/OVLGC0C6B9_v3_5EFFA623[2]
D7_OVLEW1CB9/OVLGC0C6B9_v3_5EFFA5F0[2]
D8_OVLEW1CB9/OVLGC0C6B9_v3_5EFFA5BD[2]
C1_C_0603_1608Metric_5EFFD67E[2]
U1_aitendo-MIL-2x5-cable-edge_v1_5F1FB8CC[2]

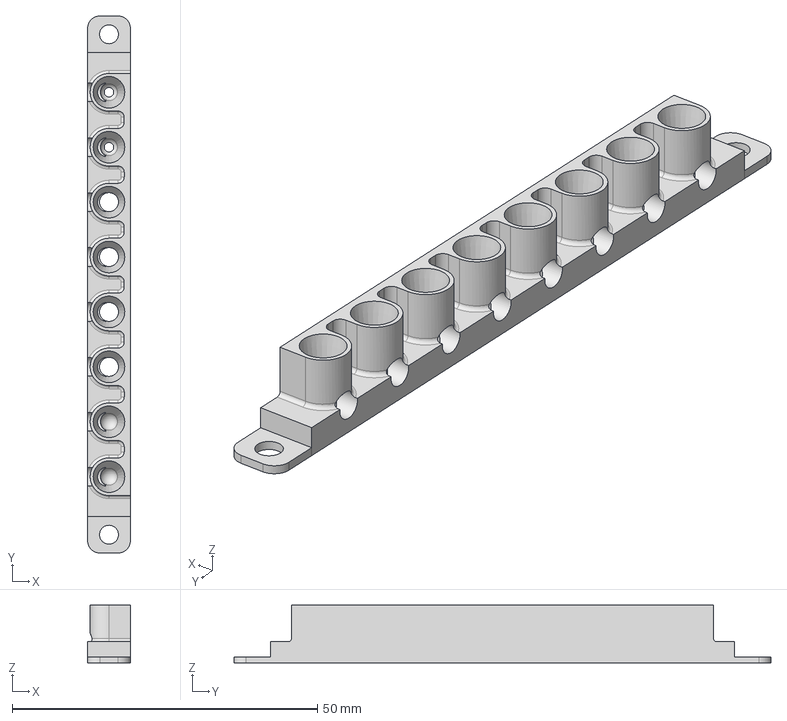
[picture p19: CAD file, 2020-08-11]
kicad/Ninja/batch01/photoarray/ver2 v15.step
7.00 x 88.0 x 9.50 mm

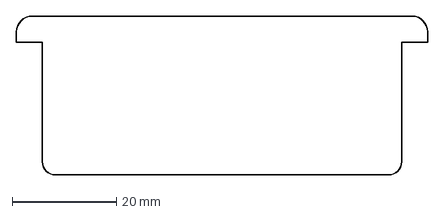
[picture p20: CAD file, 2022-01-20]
cad/2d/dxf-ver1.4/common/wood_door.dxf
79.0 x 30.5 mm

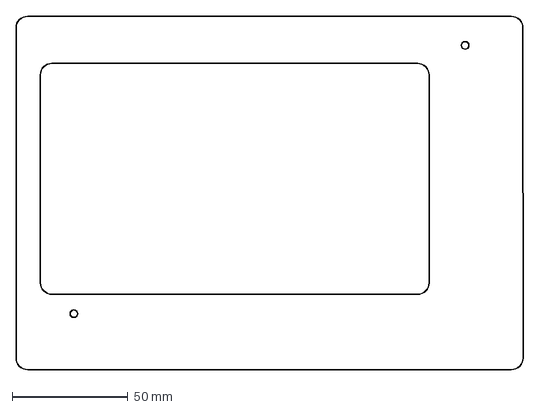
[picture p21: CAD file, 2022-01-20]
cad/2d/dxf-ver1.4/jlt-7inch/wood_lcd_cover_jtl-7inch.dxf
219.0 x 152.5 mm

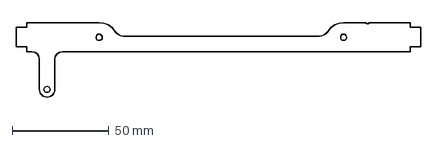
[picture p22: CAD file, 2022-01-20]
cad/2d/dxf-ver1.4/raspi/wood_lcd_holder_raspi_south.dxf
209.0 x 38.7 mm

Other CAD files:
cad/3d/3dprint/pd_cover_without_walls_x2.stl
cad/3d/aluminium/tube_holder_210806_2x8.step
cad/3d/pcb/female_header/hf_1x6.step
kicad/Ninja/batch01/photoarray/qPCR-photoarray.step
cad/2d/dxf-ver1.1/1x8_board_back.dxf
cad/2d/dxf-ver1.1/1x8_board_bottom.dxf
cad/2d/dxf-ver1.1/1x8_board_con_body.dxf
cad/2d/dxf-ver1.1/1x8_board_front.dxf
cad/2d/dxf-ver1.1/1x8_board_left.dxf
cad/2d/dxf-ver1.1/1x8_board_lid.dxf
cad/2d/dxf-ver1.1/1x8_board_middle.dxf
cad/2d/dxf-ver1.1/1x8_board_right.dxf
cad/2d/dxf-ver1.1/2x8_board_back.dxf
cad/2d/dxf-ver1.1/2x8_board_bottom.dxf
cad/2d/dxf-ver1.1/2x8_board_con_body.dxf
cad/2d/dxf-ver1.1/2x8_board_front.dxf
cad/2d/dxf-ver1.1/2x8_board_left.dxf
cad/2d/dxf-ver1.1/2x8_board_lid.dxf
cad/2d/dxf-ver1.1/2x8_board_middle.dxf
cad/2d/dxf-ver1.1/2x8_board_right.dxf
cad/2d/dxf-ver1.1/cutme_1x8_2x8_in_450x400.dxf
cad/2d/dxf-ver1.1/lid_plate.dxf
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

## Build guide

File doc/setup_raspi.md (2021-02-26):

## How to setup Raspberry Pi for Ninja qPCR safely

## Initial setup

- Download and install [Raspberry Pi Imager](https://www.raspberrypi.org/software/) to computer if it doesn't have yet.
- Stick SD card to computer.
- Choose "RASPBERRY PI OS LITE (32-BIT)" and SD card on Raspi Imager and Install.
- Move SD card from computer to Raspi.
- Connect monitor and keyboard to Raspi.
- Power on Raspi.
- Login with default ID and password ("pi" and "raspberry")
- `sudo raspi-config`
  - Keyboard setup (If need to change from US)
    - **5 Localisation Options**/**L3 Keyboard**/**Generic 105-key PC (intl.)**/**Other**/**Japanese**/**Japanese - Japanese (OADG 109A)**/**The default...**/**No compose key**
  - WiFi setup
    - **1 System Options**/**S1 Wireless LAN**/**JP Japan**(for example)/Input SSID and password/**Finish**
  - Hostname (not required)
    - **1 System Options**/**S4 Hostname**/**ninjaqpcr**(for example)/**Finish**
  - SSH setup
    - **3 Interface Options**/**P2 SSH**/**Enable**
  - SPI setup
    - **3 Interface Options**/**P4 SPI**/**Enable**
  - I2C setup
    - **3 Interface Options**/**P5 I2C**/**Enable**
- Reboot automatically
- Login with default ID and password again ("pi" and "raspberry")
- You can confirm settings by `cat /etc/wpa_supplicant/wpa_supplicant.conf`
- You can get MAC address and provided IP by `ifconfig`
- `ssh pi@(Raspi IP)` from computer in same wifi network with default ID and password ("pi" and "raspberry")
- `mkdir ~/.ssh; chmod 700 ~/.ssh`
- `vi ~/.ssh/authorized_keys` then put your public keys
- `chmod 600 ~/.ssh/authorized_keys`
- `exit`
- `ssh -i (private key) pi@(Raspi IP)` to confirm your key is working
- `sudo cp -p /etc/ssh/sshd_config /etc/ssh/sshd_config.org`
- `sudo vi /etc/ssh/sshd_config` then activate these lines
  - PermitRootLogin no
  - PasswordAuthentication no
- `sudo /etc/init.d/ssh restart`
- `sudo apt -y update; sudo apt-get -y update`

## DIY setup with git

Software update can be done manually by `git pull`.

- `sudo apt -y install git`
- `git config --global user.email "(your GitHub account email)"`
- `git config --global user.name "(your GitHub account)"`
- `git config --global push.default simple`
- `git config --global -l`
- `git config --global credential.helper store`
- `ssh-keygen -t rsa -C "(your GitHub account email)"` then just ENTER 3 times to make default private and public keys without password.
- Upload public key (~/.ssh/id_xxxx.pub) to GitHub as [Adding a new SSH key to your GitHub account](https://docs.github.com/en/github/authenticating-to-github/adding-a-new-ssh-key-to-your-github-account)
- `vi ~/.ssh/config` to write this 
  ```
  Host github
    User git
    Port 22
    HostName github.com
    IdentityFile ~/.ssh/id_xxxx
    IdentitiesOnly yes
  ```
- `chmod 600 ~/.ssh/config`
- `git clone github:hisashin/Ninja-qPCR.git`
- `curl -L https://raw.githubusercontent.com/hisashin/Ninja-qPCR/master/src/greengrass/setup.sh | sudo sh`
  - isc-dhcp-server may be failed to startup if you're using WiFi. It's ok for now and just ignore.
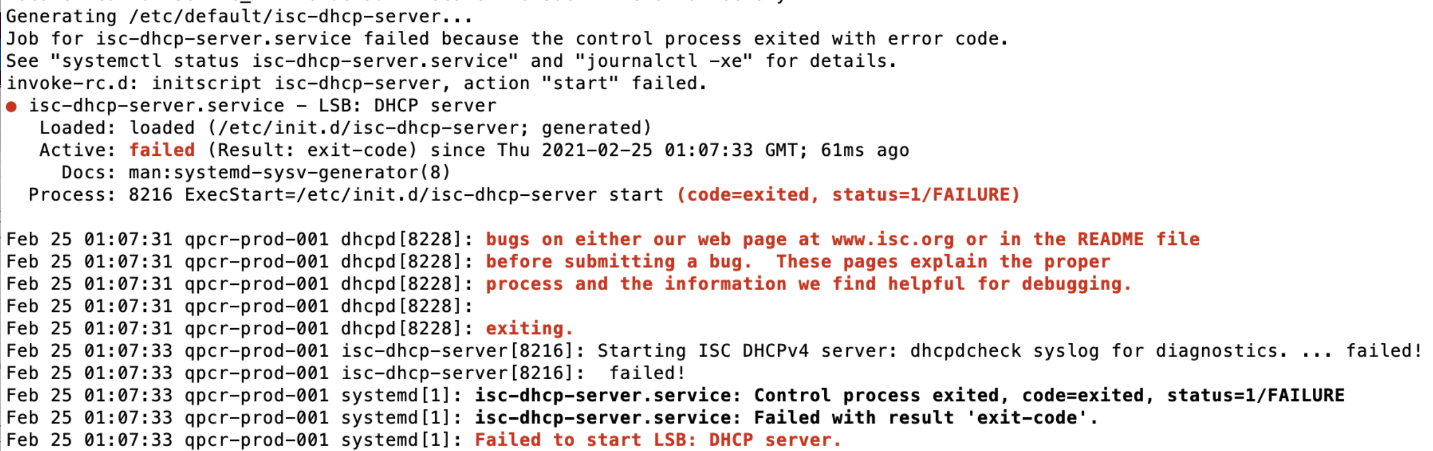
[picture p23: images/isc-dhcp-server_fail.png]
fail
      
- `sudo ln -f -s Ninja-qPCR/src-prod/src /usr/local/ninjaqpcr`
- `cd /usr/local/ninjaqpcr/qpcr`
- `echo y | sudo npm update`
- `cd /usr/local/ninjaqpcr/console/server`
- `echo y | sudo npm update`
- `sudo cp /etc/rc.local /etc/rc.local.orig`
- `sed -i "s#exit 0#/usr/local/ninjaqpcr/startup/startup.sh;\n\nexit 0#" /etc/rc.local`

## PRO setup with [AWS Greengrass](https://aws.amazon.com/greengrass/)

Ninja qPCR software will be installed and updated to the latest automatically when it's added to the proper Greengrass group.

[Setting up a Raspberry Pi](https://docs.aws.amazon.com/greengrass/latest/developerguide/setup-filter.rpi.html)

- `curl -L https://raw.githubusercontent.com/hisashin/Ninja-qPCR/master/src/greengrass/setup.sh | sudo sh`
  - isc-dhcp-server may be failed to startup if you're using WiFi. It's ok for now and just ignore.
    fail  
- `sudo reboot`

[Configure AWS IoT Greengrass on AWS IoT](https://docs.aws.amazon.com/greengrass/v1/developerguide/gg-config.html)

- Open [Create core device](https://ap-northeast-1.console.aws.amazon.com/iot/home?region=ap-northeast-1#/greengrass/v2/cores/create) on AWS Console
  - example name of core device : qpcr-dev-001
  - example name of group : qpcr-dev
- Publish **temporary** security credentials using AWS STS trust relationship
  - `aws sts assume-role --role-arn arn:aws:iam::123456789:role/(role-name) --role-session-name "qpcr-dev-temp" --profile (proper IAM) > assume-role-output.txt` on computer
    - my case `aws sts assume-role --role-arn arn:aws:iam::314407188943:role/greengrass --role-session-name qpcr-dev-001 --duration-seconds 3600 --profile gg_publisher` to sysout credentials
- `ssh -i (private key) pi@(Raspi IP)`
- `export AWS_ACCESS_KEY_ID=(Credentials.AccessKeyId)`
- `export AWS_SECRET_ACCESS_KEY=(Credentials.SecretAccessKey)`
- `export AWS_SESSION_TOKEN=(Credentials.SessionToken)`
- Run commands shown at the bottom end of **Create core device** page
  my case 
  - `curl -s https://d2s8p88vqu9w66.cloudfront.net/releases/greengrass-nucleus-latest.zip > greengrass-nucleus-latest.zip && unzip greengrass-nucleus-latest.zip -d GreengrassCore`
  - `sudo -E java -Droot="/greengrass/v2" -Dlog.store=FILE -jar ./GreengrassCore/lib/Greengrass.jar --aws-region ap-northeast-1 --thing-name qpcr-dev-001 --thing-group-name qpcr-dev --component-default-user ggc_user:ggc_group --provision true --setup-system-service true --deploy-dev-tools true`
  - `sudo tail -f /greengrass/v2/logs/greengrass.log` to check log
- Finish Create core device and wait a while to show up added thing qpcr-dev-001
- `sudo reboot`

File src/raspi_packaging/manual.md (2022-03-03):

# Installation
* Insert SD card to Mac
* Install Raspberry Pi OS LITE to a SD card (>8GB) with Imager (v1.4)

# Setup
* Insert SD card to RasPi board
* Power on
* Login (user=pi, password=raspberry)
* Config `sudo raspi-config`
  * Change keyboard layout (Localisation Options > Change Keyboard Layout > Change Keyboard Layout > Generic 105-key PC (intl.) > Japanese)
  * Localisation Options > Change WLAN Country
  * Change User Password
  * Open "Network Options > Hostname" and input "ninjaqpcr". This config is applied to mDNS.
  * Enable functionalities
    * Interfacing options > I2C
    * Interfacing options > SSH
  * Network config (Wireless LAN)
    * Input Country (JP), SSID and password
      * or `sudo wpa_passphrase <SSID> <passphrase> | sudo tee -a /etc/wpa_supplicant/wpa_supplicant.conf`
* Finish raspi-config and reboot (in dialog)

# Add SSH key (from PC)
* `ssh-copy-id pi@ninjaqpcr.local` (Remove a line containing "ninjaqpcr.local" from ~/.ssh/known_hosts if needed)
* Now you can login by just typing `ssh pi@ninjaqpcr.local`

# Install packages (apt & npm)
```
sudo apt update
sudo apt install nodejs npm hostapd isc-dhcp-server wiringpi libcap2-bin lightdm
sudo apt-get update --fix-missing
sudo setcap cap_net_bind_service=+ep /usr/bin/node
sudo npm install --global http-server
```

Create directories

```
sudo mkdir /usr/local/ninjaqpcr
sudo chown pi /usr/local/ninjaqpcr
mkdir -p /usr/local/ninjaqpcr/console/client/dist
mkdir ~/ninjaqpcr
mkdir ~/ninjaqpcr/user_data
mkdir ~/ninjaqpcr/user_data/protocol
mkdir ~/ninjaqpcr/user_data/experiment

```

# Install apps (from PC)

```
cd /Users/maripo/git/Ninja-qPCR/src
scp qpcr/user_data/protocol/* pi@ninjaqpcr.local:~/ninjaqpcr/user_data/protocol
./deploy.sh
./deploy_update.sh # Update packages
```

# Register startup script
* `sudo vi /etc/rc.local`
* Add `/usr/local/ninjaqpcr/startup/startup.sh` above line `exit 0`

# Define global env variables
* `sudo vi /etc/environment`
* Add lines below
```
NINJAQPCR_USER_DATA=/home/pi/ninjaqpcr/user_data
NINJAQPCR_HOME=/usr/local/ninjaqpcr
```

# Launch Chromium on GUI launch
* `mkdir ~/.config/autorun`
* `vi ~/.config/autorun/ninjaqpcr.desktop`
```
[Desktop Entry]
Name=Ninja-qPCR
Exec=/usr/bin/chromium-browser --noerrdialogs --disable-infobars --kiosk http://localhost:8080?kiosk=true
Type=Application
```

# Disable GPIO interrupts (for rpio.poll)
Add the following line to /boot/config.txt
```
dtoverlay=gpio-no-irq

```

# Delete logs and settings
```
sudo rm -rf /var/log/*
echo "" > ~/.ssh/authorized_keys
sudo cp /usr/local/ninjaqpcr/network_conf_app/wpa_supplicant_header.txt /etc/wpa_supplicant/wpa_supplicant.conf
rm -f ~/.bash_history
```

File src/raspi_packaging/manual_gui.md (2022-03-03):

# Flash RPi image to SD card
* Insert SD card (>8GB) to Mac
* Install Raspberry Pi OS (32-bit) with Imager (v1.4)

# Setup (by touchscreen interface)
* Insert SD card to RasPi

## Touchscreen of Mouse
* Connect RPi's USB port and the touchscreen's "touch" port
  * Connecting both touch interface via USB hub and keyboard does not work correctly.
* Connect RPI and the touchscreen by HDMI cable
* Power on (GUI starts)
* (By touchscreen interface) Left-top menu > Preferences > Raspberry Pi Configuration > System > Boot / Auto Login > To Console Autologin
* (By touchscreen interface) Left-top menu > Logout > Shutdown

## Keyboard
* Attach a keyboard to RPi's USB port
* Waiting for X startup
* Exit X by pressing Ctrl + Alt + F1

# Setup by CLI
* Connect items
  * Power the touchscreen by 5V AC adapter (instead of RPi's USB port)
  * Attach a keyboard to RPi's USB port
* Login (user=pi, password=raspberry)
* Config `sudo raspi-config`
  * Change keyboard layout (Localisation Options > Keyboard > Generic 105-key PC (intl.) > Japanese)
    * Enable X shutdown by Ctrl+Alt+BS
  * Localisation Options > WLAN Country
    * Select your country based on physical location
  * Change User Password (System options > Password)
  * Open "System options > Hostname" and input "ninjaqpcr". This config is applied to mDNS.
  * Enable functionalities
    * Interfacing options > I2C
    * Interfacing options > SSH
  * Network config (System options > Wireless LAN)
    * Input Country (JP), SSID and password
      * or `sudo wpa_passphrase <SSID> <passphrase> | sudo tee -a /etc/wpa_supplicant/wpa_supplicant.conf`
  * Enable GUI auto-login
    * System options > Boot / Auto Login : Detktop autologin
  * Disable screen sleep
    * Display Options > Screen Blanking > NO
  * Display Options > Underscan (Remove black borders)
  * Exit raspi-config
* `sudo reboot`

# Add SSH key (from PC)
* `ssh-copy-id pi@ninjaqpcr.local` (Remove a line containing "ninjaqpcr.local" from ~/.ssh/known_hosts if needed)
* Now you can login by just typing `ssh pi@ninjaqpcr.local`

# Install packages (apt & npm)
```
sudo apt update
# sudo apt install nodejs npm hostapd isc-dhcp-server wiringpi libcap2-bin
sudo apt install nodejs npm hostapd isc-dhcp-server libcap2-bin lightdm
sudo apt-get update --fix-missing
sudo setcap cap_net_bind_service=+ep /usr/bin/node
sudo npm install --global http-server
```

Create directories

```
sudo mkdir /usr/local/ninjaqpcr
sudo chown pi /usr/local/ninjaqpcr
mkdir -p /usr/local/ninjaqpcr/console/client/dist
mkdir ~/ninjaqpcr
mkdir ~/ninjaqpcr/user_data
mkdir ~/ninjaqpcr/user_data/protocol
mkdir ~/ninjaqpcr/user_data/experiment
mkdir ~/.config/autorun

```

# Install apps (from PC)

```
cd /Users/maripo/git/Ninja-qPCR/src
scp qpcr/user_data/protocol/* pi@ninjaqpcr.local:~/ninjaqpcr/user_data/protocol
./deploy.sh
./deploy_update.sh # Update packages
```

# Set X Startup script
```
sudo vi /etc/xdg/lxsession/LXDE-pi/autostart
```
and paste

```
@lxpanel --profile LXDE-pi
@pcmanfm --desktop --profile LXDE-pi
@xscreensaver -no-splash

```

/usr/bin/chromium-browser --noerrdialogs --disable-infobars --kiosk http://localhost:8080?kiosk=true

# Register startup script
* `sudo vi /etc/rc.local`
* Add `/usr/local/ninjaqpcr/startup/startup.sh` above line `exit 0`

# Define global env variables
* `sudo vi /etc/environment`
* Add lines below
```
NINJAQPCR_USER_DATA=/home/pi/ninjaqpcr/user_data
NINJAQPCR_HOME=/usr/local/ninjaqpcr
```

# Disable GPIO interrupts (for rpio.poll)
Add the following line to /boot/config.txt
```
dtoverlay=gpio-no-irq

```

# Display config

vi /boot/config.txt

framebuffer_width=1024
framebuffer_height=600

# Delete logs and settings
```
sudo rm -rf /var/log/*
echo "" > ~/.ssh/authorized_keys
sudo cp /usr/local/ninjaqpcr/network_conf_app/wpa_supplicant_header.txt /etc/wpa_supplicant/wpa_supplicant.conf
rm -f ~/.bash_history
```

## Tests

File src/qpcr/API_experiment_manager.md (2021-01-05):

# class ExperimentManager

(TODO)

## generateExperimentId ()

## getSummaries (filter, order, onLoad, onError)

## getLatestExperiment (onLoad, onError)

## getExperiment (id, onLoad, onError)

## generateExperimentSummary (experimentLog)

## saveExperimentLog (experimentLog, onSuccess, onError)

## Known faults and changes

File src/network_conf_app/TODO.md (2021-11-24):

* Support multiple access points
* Load existing settings
* Support "Run Device as an Access Point"
* Backup & restore wpa_supplicant.conf
* Reboot after saving
* Allow empty password

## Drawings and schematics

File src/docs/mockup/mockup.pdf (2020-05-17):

# Top

# Ninja-qPCR

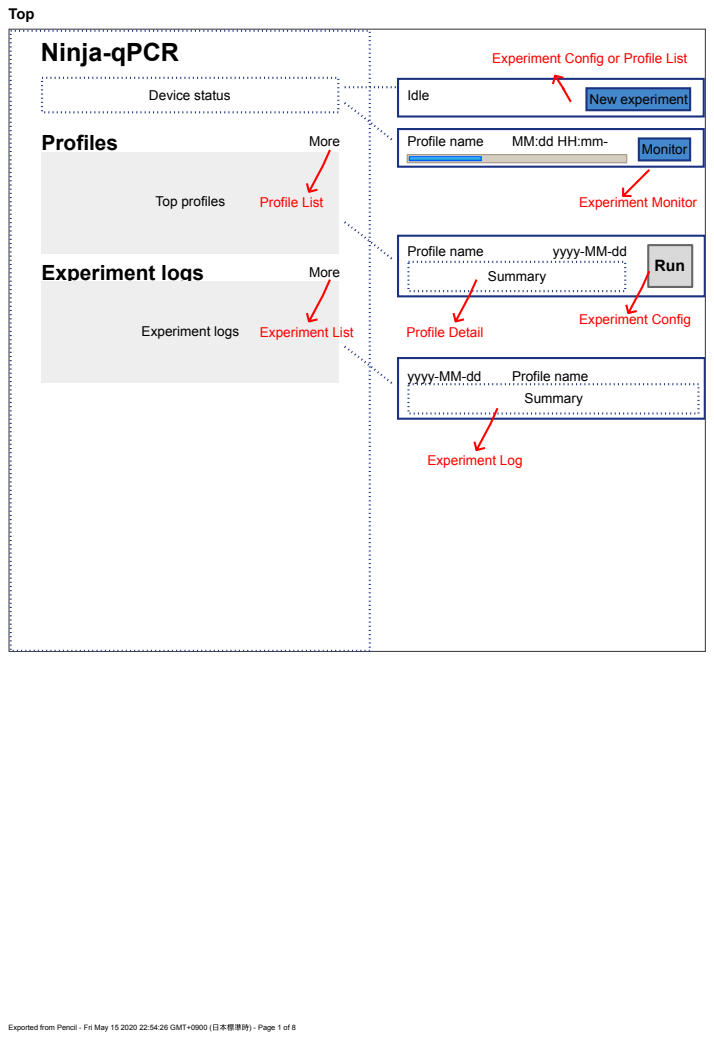
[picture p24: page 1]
Device status; Profile name; Summary; Run; More; Profiles; Experiment logs; Profile name Summary; Top profiles; Monitor; Experiment Monitor; Experiment Log; Experiment List; Profile List

Experiment Config or Profile List

New experiment Idle

yyyy-MM-dd

Experiment Config Profile Detail

Exported from Pencil - Fri May 15 2020 22:54:26 GMT+0900 (⽇本標準時) - Page 1 of 8

# Profile List

# Profile name

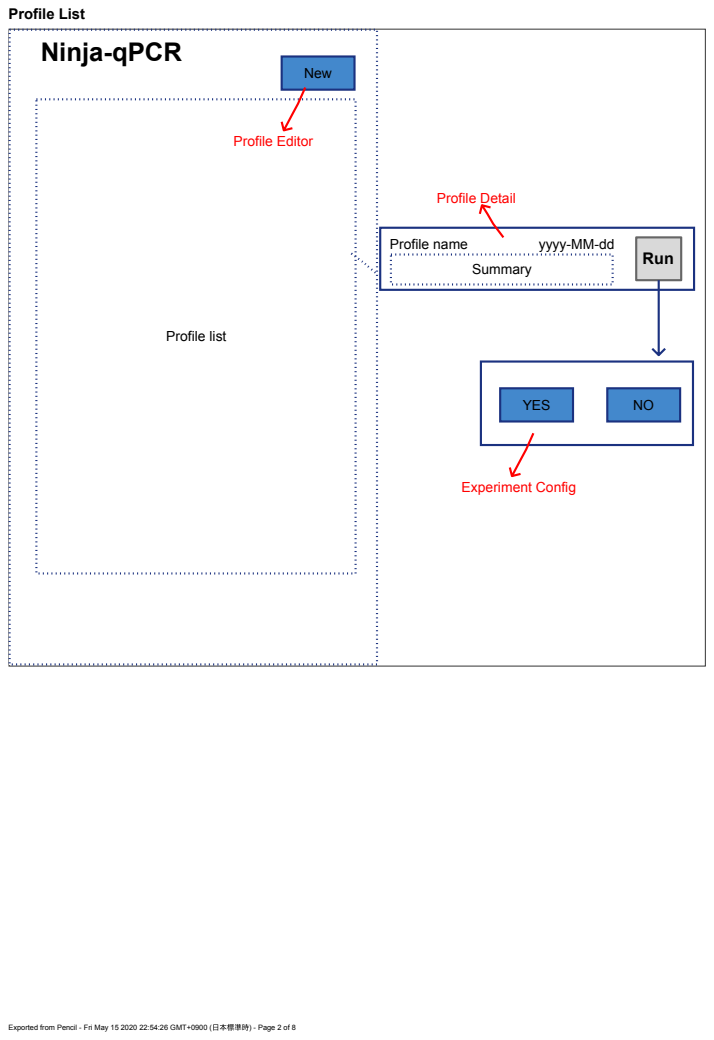
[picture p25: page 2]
Profile list; Summary; Run; YES; New; Profile Editor; Experiment Config; Profile Detail

yyyy-MM-dd

Exported from Pencil - Fri May 15 2020 22:54:26 GMT+0900 (⽇本標準時) - Page 2 of 8

# Profile Detail

# Name

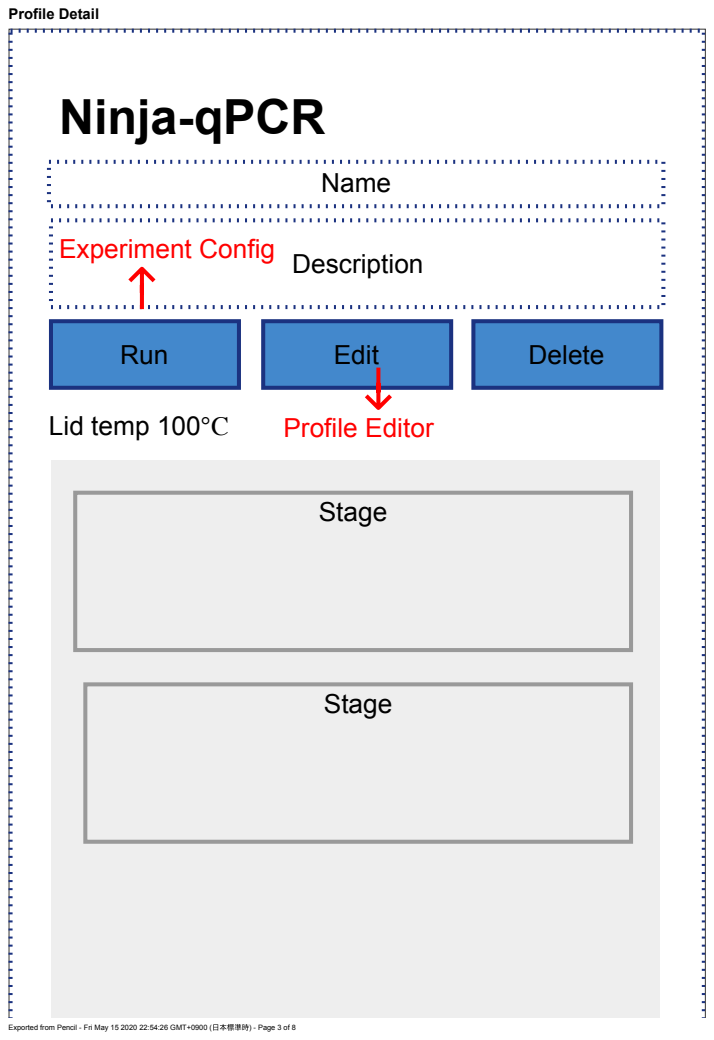
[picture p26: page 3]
Run; Edit; Ninja-qPCR; Delete; Stage; Lid temp 100℃; Description; Profile Editor; Experiment Config

Exported from Pencil - Fri May 15 2020 22:54:26 GMT+0900 (⽇本標準時) - Page 3 of 8

# Profile Editor

## Name

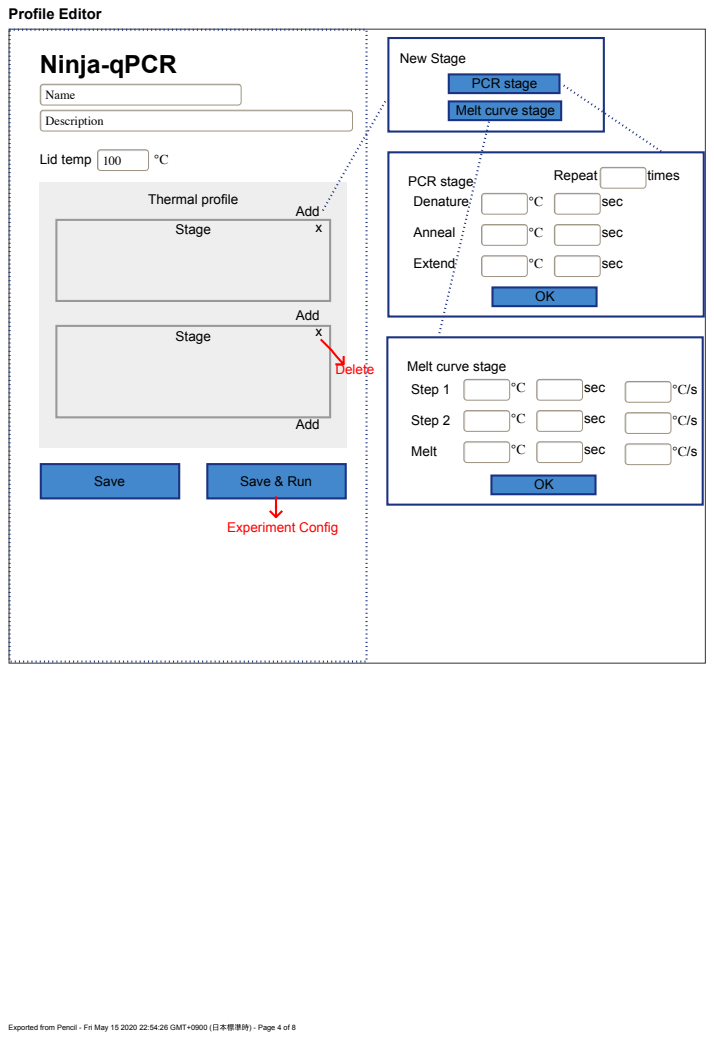
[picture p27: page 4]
Save; Description; Thermal profile; Lid temp 100; Save & Run; PCR stage; Stage; Add; Denature; sec; Repeat; times; Anneal; Extend; Step 1; Step 2; Melt; Experiment Config; New Stage; Delete

PCR stage
Melt curve stage

Exported from Pencil - Fri May 15 2020 22:54:26 GMT+0900 (⽇本標準時) - Page 4 of 8

# Experiment Logs

## Experiment Logs

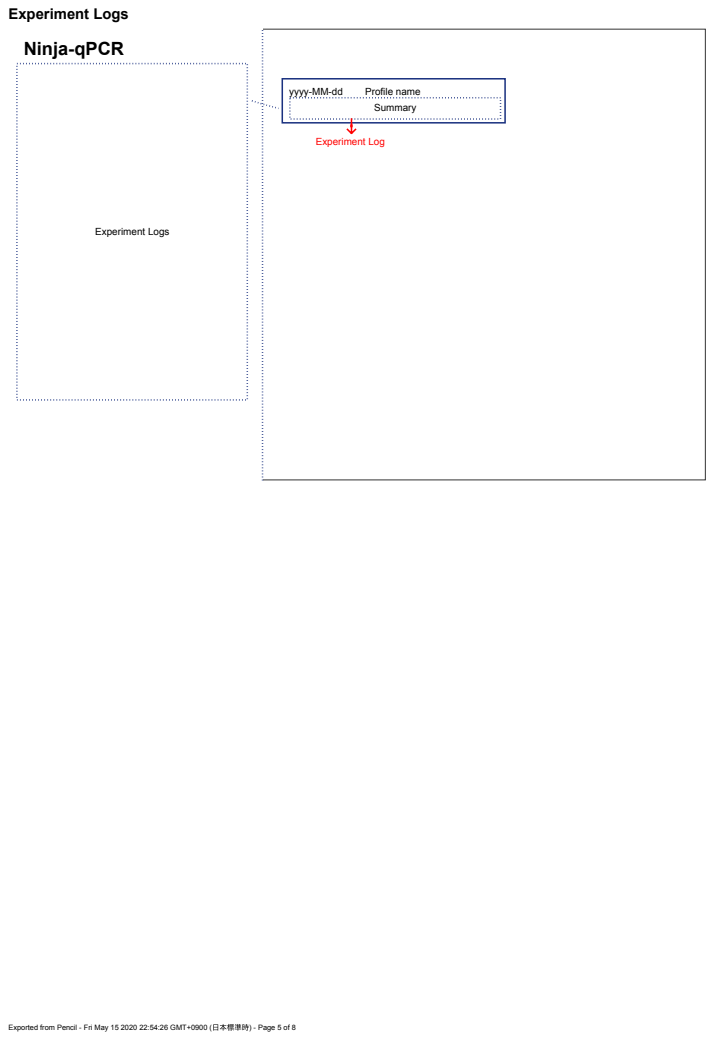
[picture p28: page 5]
Profile name Summary; Experiment Log

yyyy-MM-dd

Exported from Pencil - Fri May 15 2020 22:54:26 GMT+0900 (⽇本標準時) - Page 5 of 8

# Experiment Config

## Profile summary

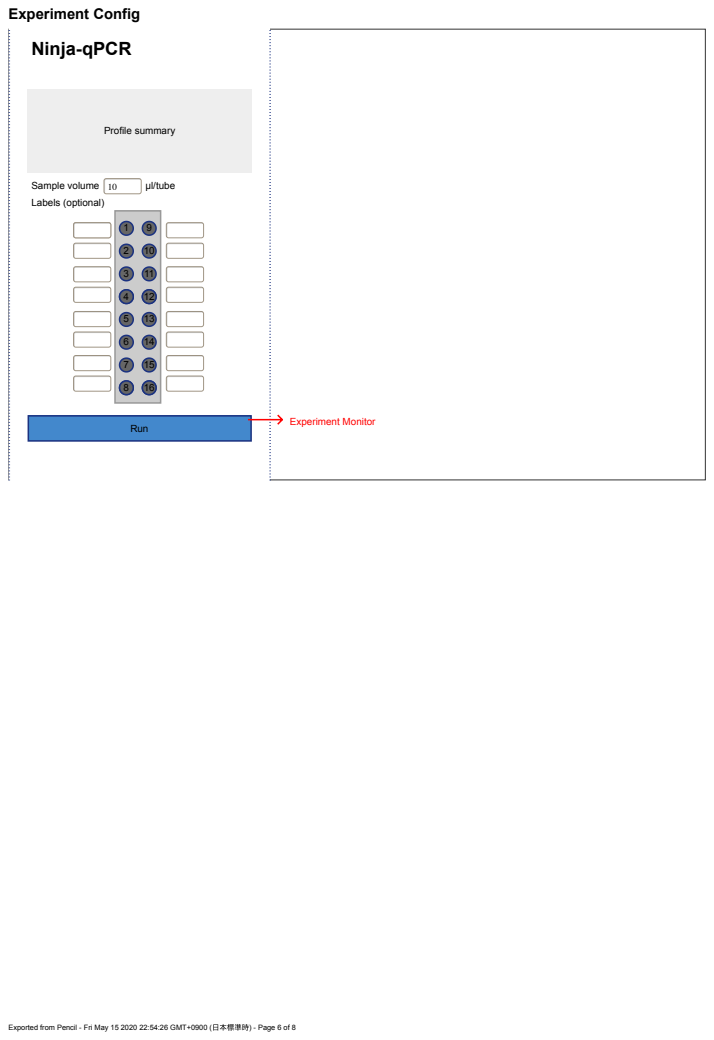
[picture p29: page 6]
Run; Experiment Monitor; Sample volume 10; μl/tube; Labels (optional)

Exported from Pencil - Fri May 15 2020 22:54:26 GMT+0900 (⽇本標準時) - Page 6 of 8

# Experiment Log

## Profile summary

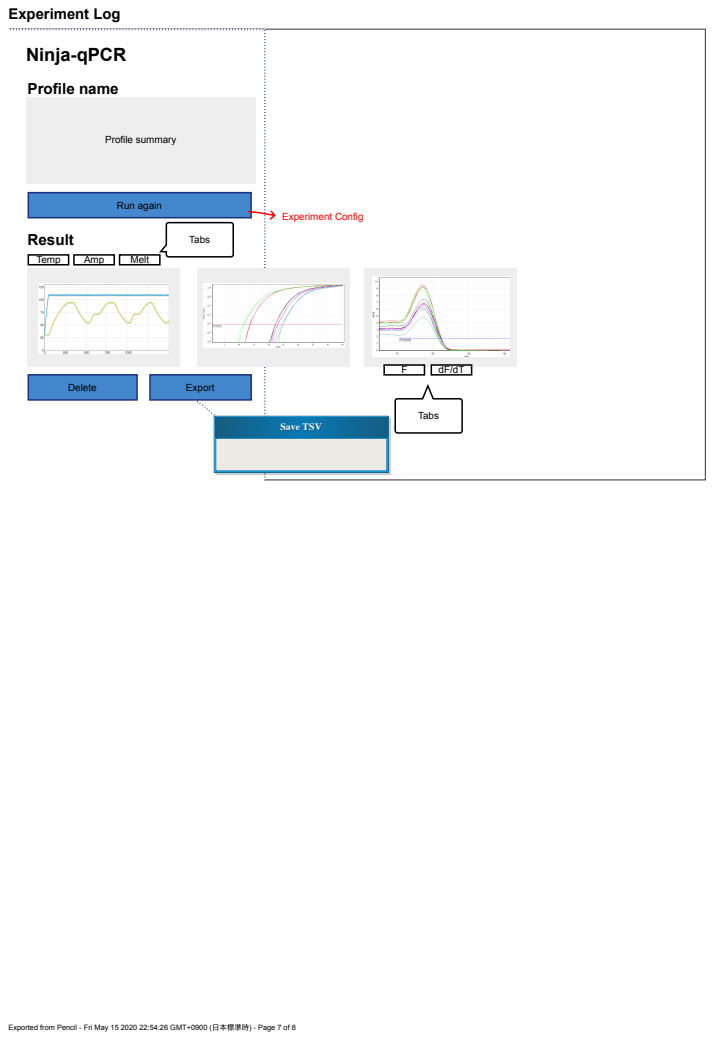
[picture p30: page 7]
Temperature; Fluorescence; Melt curve; Temp; Amp; Melt; Tabs; Run again; Result; Profile name; Delete; Export; SSaavvee TTSSVV; Experiment Config

Exported from Pencil - Fri May 15 2020 22:54:26 GMT+0900 (⽇本標準時) - Page 7 of 8

# Experiment Monitor

# Profile name

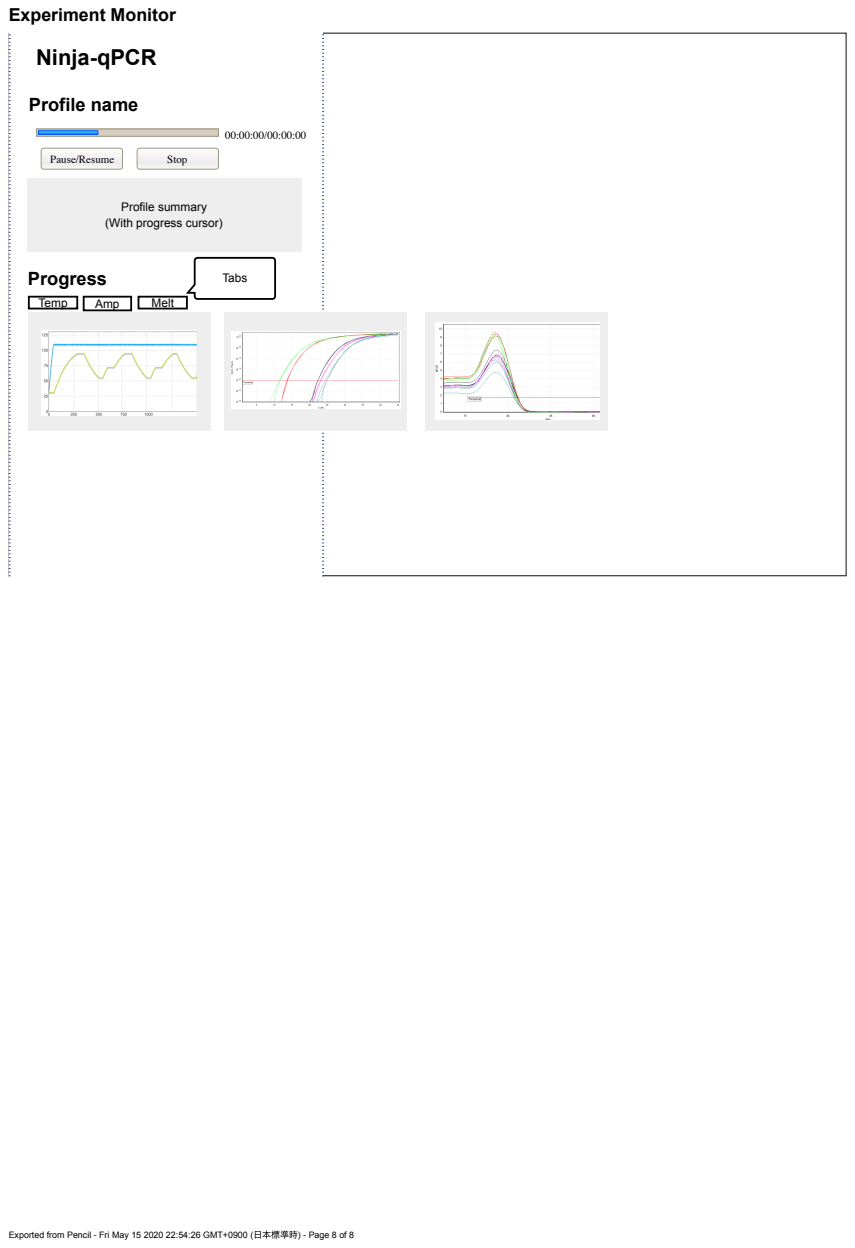
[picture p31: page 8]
Temperature; Fluorescence; Melt curve; Temp; Amp; Melt; Progress; Tabs; Pause/Resume; Stop

Profile summary
(With progress cursor)

Exported from Pencil - Fri May 15 2020 22:54:26 GMT+0900 (⽇本標準時) - Page 8 of 8

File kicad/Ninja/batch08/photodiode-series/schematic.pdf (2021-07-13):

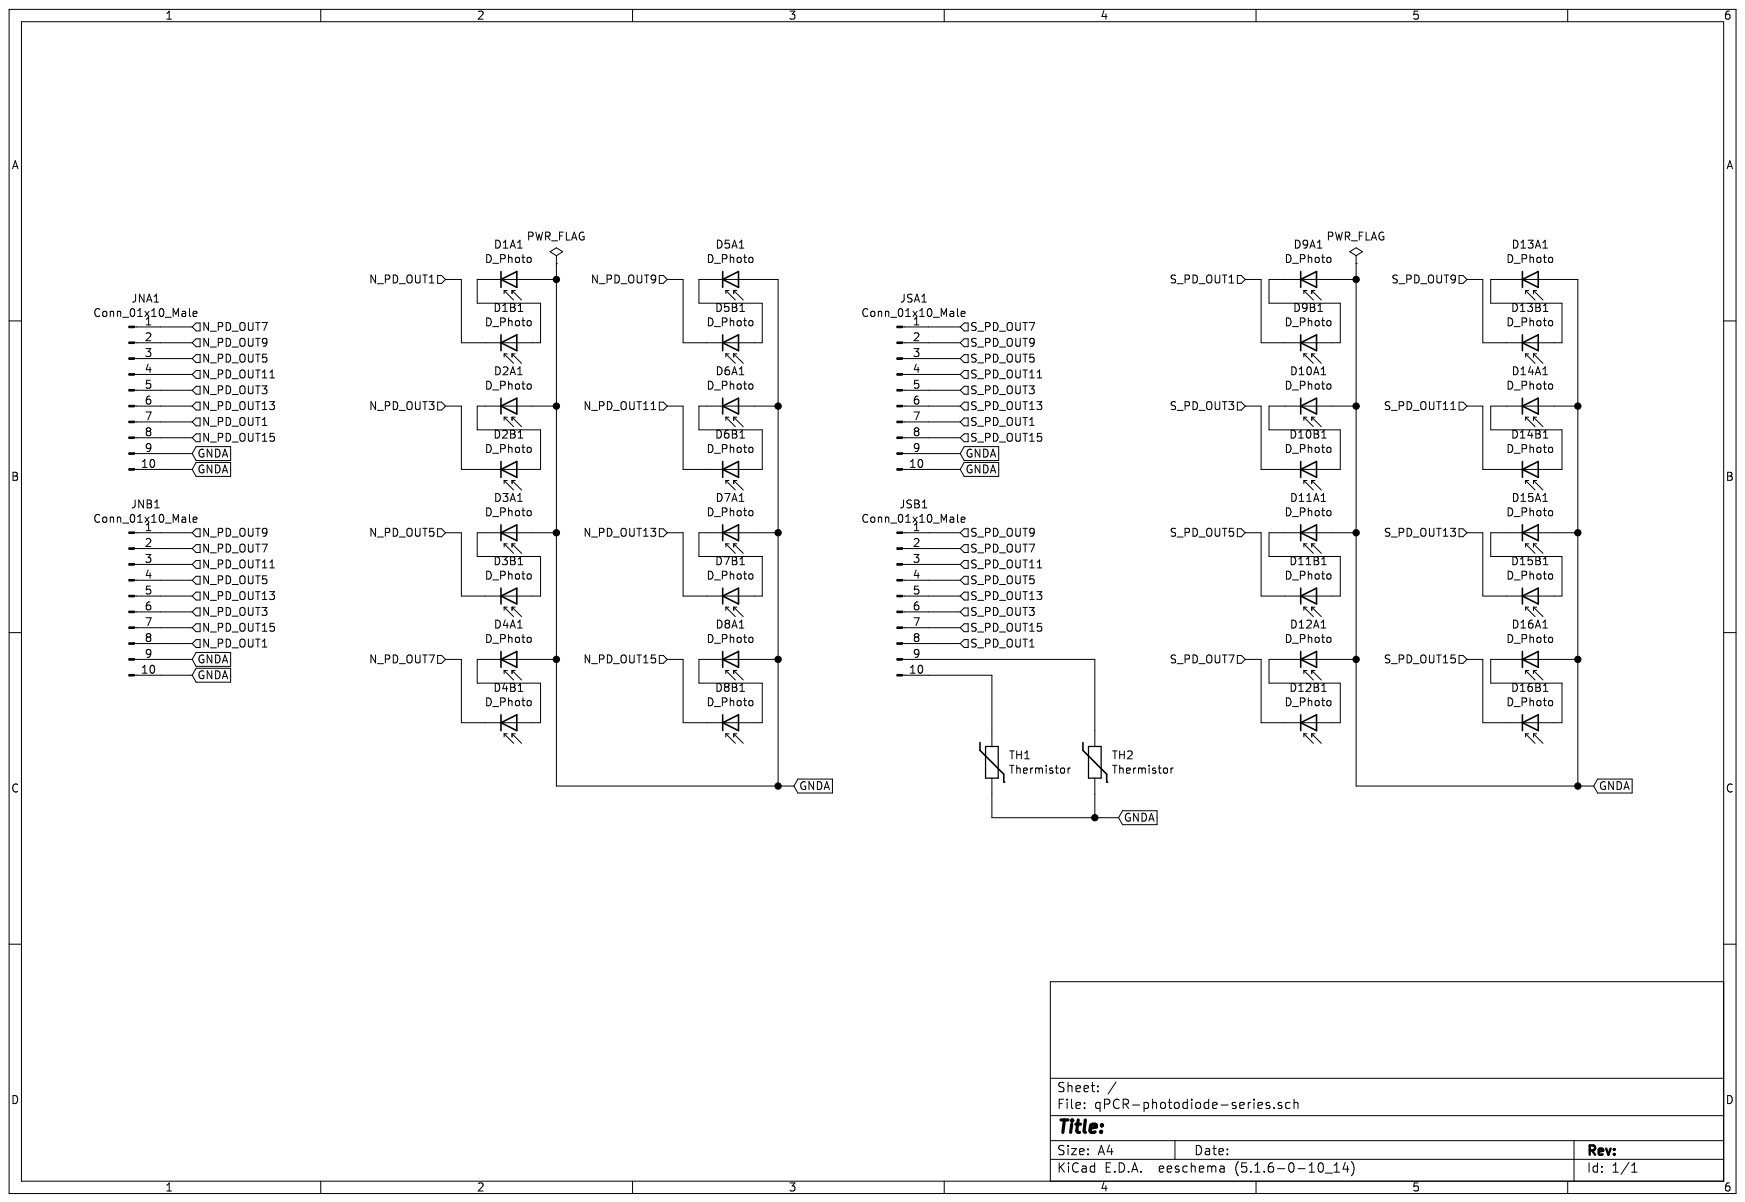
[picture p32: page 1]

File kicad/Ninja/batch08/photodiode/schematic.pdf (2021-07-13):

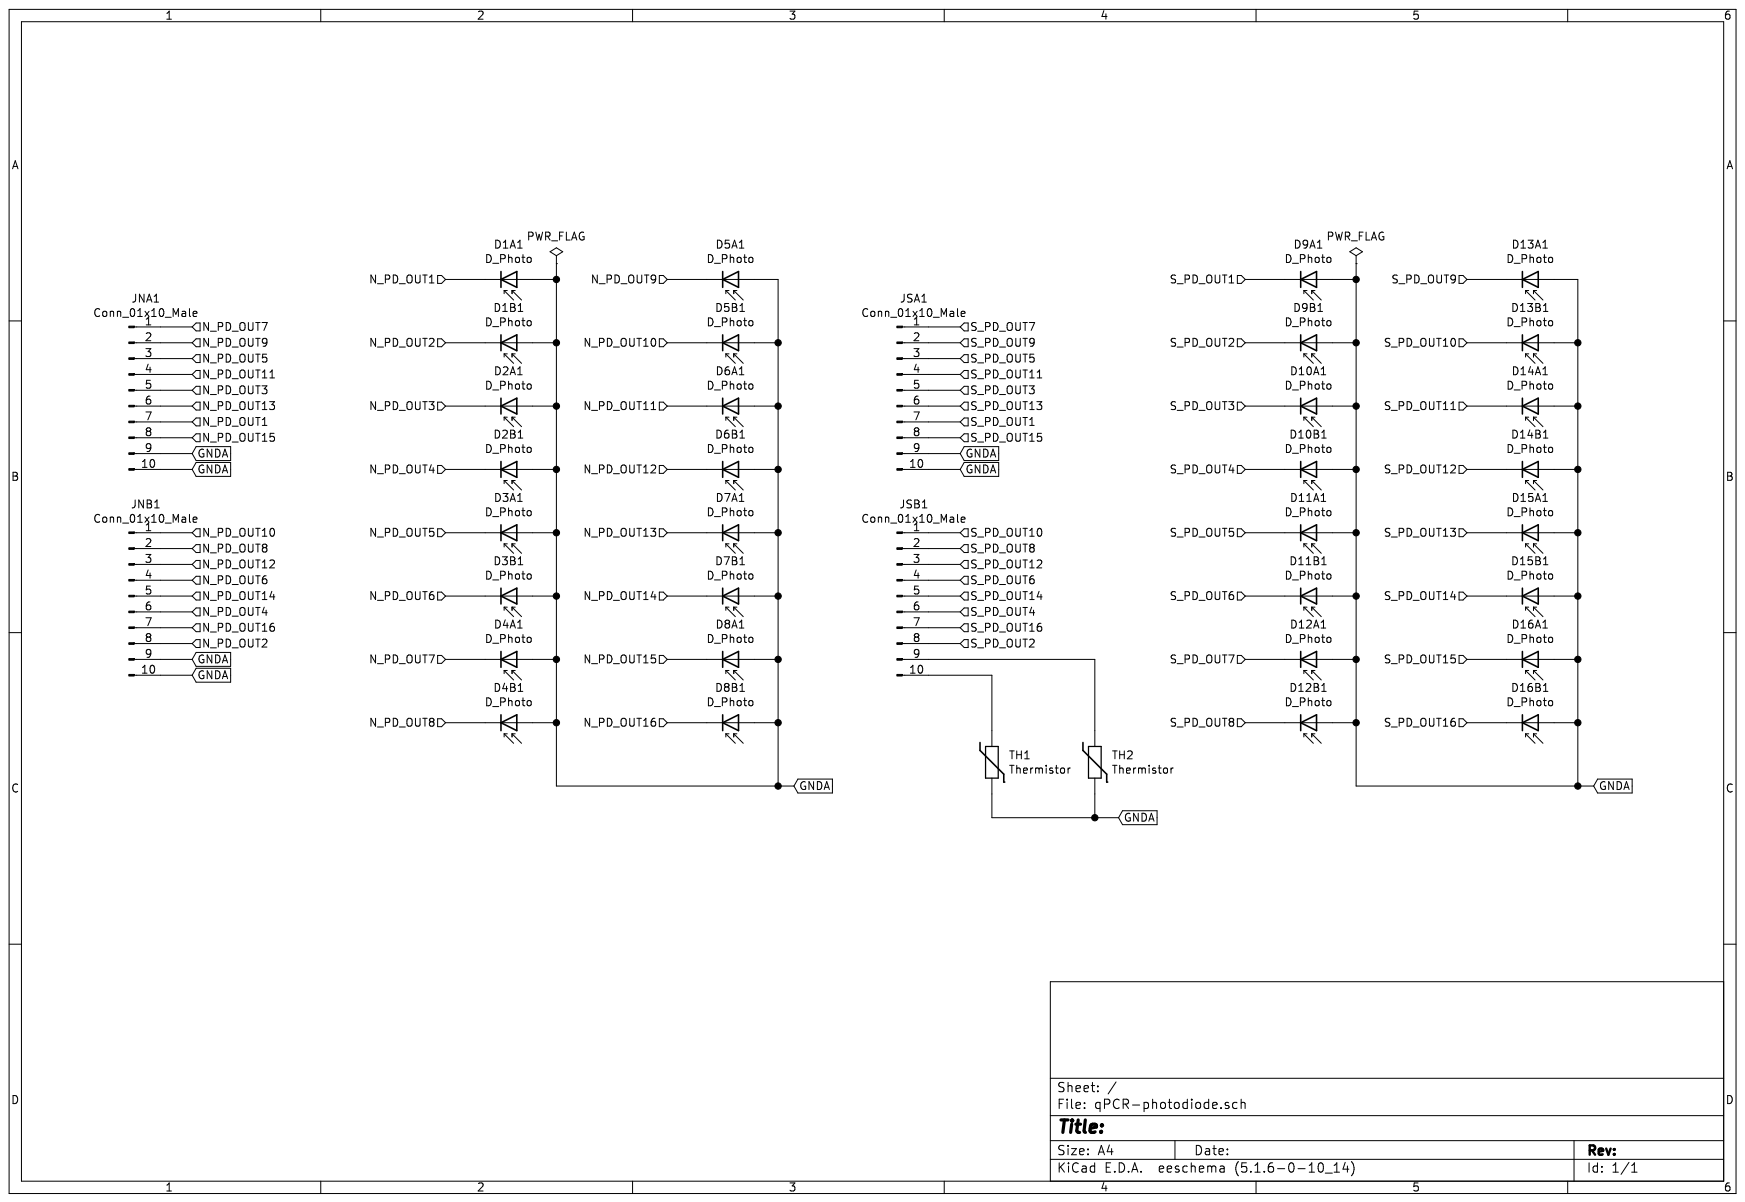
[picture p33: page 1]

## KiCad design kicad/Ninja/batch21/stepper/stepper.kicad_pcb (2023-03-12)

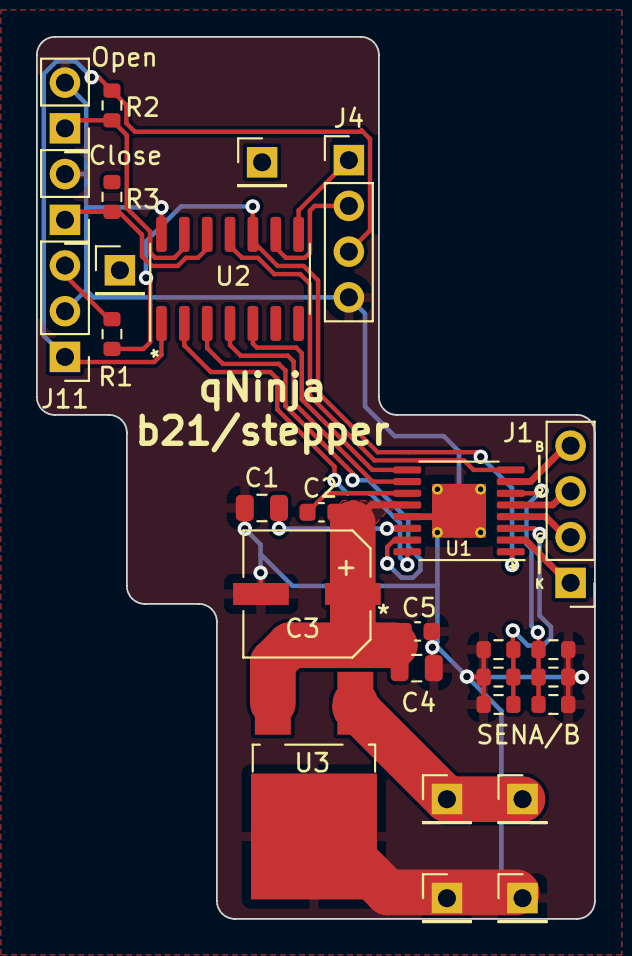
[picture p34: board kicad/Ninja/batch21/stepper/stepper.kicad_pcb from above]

Board: 2 copper layers, 31.0 x 49.0 mm, 28 parts (0 on the bottom side), 23 nets.

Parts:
C1: 4.7uF; C_0805_2012Metric
C2, C5: 0.1uF; C_0603_1608Metric
C3: 100uF; 35TZV100M6.3X8
C4: 10uF; C_0805_2012Metric
J1: Conn_01x04_Male; PinHeader_1x04_P2.54mm_Vertical
J3, J5, J6, J7, J9, J10: Conn_01x01_Pin; PinHeader_1x01_P2.54mm_Vertical
J4: Conn_01x04_Pin; PinHeader_1x04_P2.54mm_Vertical
J11: Conn_01x03_Pin; PinHeader_1x03_P2.54mm_Vertical
J12, J13: Conn_01x02_Pin; PinHeader_1x02_P2.54mm_Vertical
R1, R2, R3: 4.7k; R_0603_1608Metric
RSENA1, RSENA2, RSENA3: R; R_0603_1608Metric
RSENB1, RSENB2, RSENB3: R; R_0603_1608Metric
U1: MP6507GF-Z; TSSOP-16-1EP_4.4x5mm_P0.65mm_EP3x3mm_ThermalVias
U2: ATtiny404-SS; SOIC-14_3.9x8.7mm_P1.27mm
U3: REG_TO252-3

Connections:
/3V3D: J4.3, J11.1, R2.2, U2.1 (VCC)
/12VB: J5.1, J6.1, U3.1 (VIN)
/AIN1: U1.16 (AIN1), U2.2 (PA4)
/AIN2: U1.15 (AIN2), U2.3 (PA5)
/BIN1: U1.10 (BIN2), U2.4 (PA6)
/BIN2: U1.9 (BIN1), U2.5 (PA7)
/DCLOSE: J13.1, R3.1, U2.12 (PA2)
/DOPEN: J12.1, R2.1, U2.13 (PA3)
/FAULT: U1.8 (FAULT), U2.11 (PA1)
/I2C_SCL: J4.2, U2.9 (PB0)
/I2C_SDA: J4.1, U2.8 (PB1)
/NSLEEP: R1.1, U1.1 (NSLEEP), U2.10 (~RESET/PA0)
/SENA: RSENA1.1, RSENA2.1, RSENA3.1, U1.3 (SENA)
/SENB: RSENB1.2, RSENB2.2, RSENB3.2, U1.6 (SENB)
/UPDI: J11.3, R1.2
/VIN: C2.2, C3.1, C4.1, C5.1, U1.12 (VIN), U3.2 (VOUT)
GND: C1.1, C3.2, C4.2, C5.2, J4.4, J9.1, J10.1, J11.2, J12.2, J13.2, RSENA1.2, RSENA2.2, RSENA3.2, RSENB1.1, RSENB2.1, RSENB3.1, U1.13 (GND), U1.17 (EPAD), U2.14 (GND), U3.3 (GND)
unnamed: J1.1, U1.2 (AOUT1)
unnamed: J1.2, U1.4 (AOUT2)
unnamed: J1.3, U1.5 (BOUT2)
unnamed: J1.4, U1.7 (BOUT1)
unnamed: C2.1, U1.11 (BST)
unnamed: C1.2, U1.14 (VDD)

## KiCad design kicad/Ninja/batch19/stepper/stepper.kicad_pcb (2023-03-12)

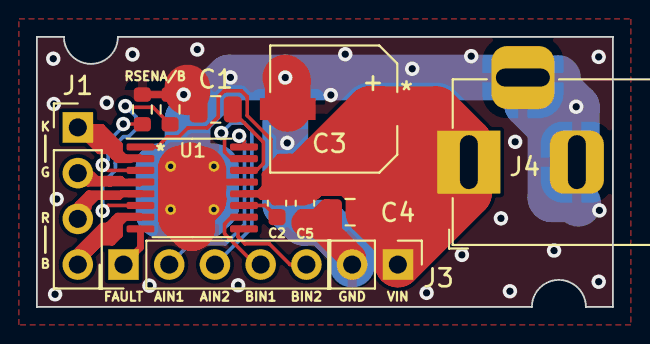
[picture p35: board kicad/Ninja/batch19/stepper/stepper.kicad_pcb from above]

Board: 2 copper layers, 32.0 x 15.0 mm, 12 parts (0 on the bottom side), 15 nets.

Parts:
C1: 4.7uF; C_0805_2012Metric
C2: 0.1uF; C_0603_1608Metric
C3: 100uF; 35TZV100M6.3X8
C4: 10uF; C_0805_2012Metric
C5: 0.1uF(Low ESR ceramic); C_0603_1608Metric
J1: Conn_01x04_Male; PinHeader_1x04_P2.54mm_Vertical
J2: Conn_01x05_Male; PinHeader_1x05_P2.54mm_Vertical
J3: Conn_01x02_Male; PinHeader_1x02_P2.54mm_Vertical
J4: Barrel_Jack_Switch; BarrelJack_Horizontal
RSENA1: R; R_0603_1608Metric
RSENB1: R; R_0603_1608Metric
U1: MP6507GF-Z; TSSOP-16-1EP_4.4x5mm_P0.65mm_EP3x3mm_ThermalVias

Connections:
/AIN1: J2.2, U1.16 (AIN1)
/AIN2: J2.3, U1.15 (AIN2)
/BIN1: J2.4, U1.10 (BIN2)
/BIN2: J2.5, U1.9 (BIN1)
/FAULT: J2.1, U1.8 (FAULT)
/VIN: C2.2, C3.1, C4.1, C5.1, J3.1, J4.1, U1.1 (NSLEEP), U1.12 (VIN)
GND: C1.1, C3.2, C4.2, C5.2, J3.2, J4.2, J4.3, RSENA1.2, RSENB1.2, U1.13 (GND), U1.17 (EPAD)
unnamed: C1.2, U1.14 (VDD)
unnamed: C2.1, U1.11 (BST)
unnamed: J1.1, U1.2 (AOUT1)
unnamed: J1.2, U1.4 (AOUT2)
unnamed: J1.3, U1.5 (BOUT2)
unnamed: J1.4, U1.7 (BOUT1)
unnamed: RSENA1.1, U1.3 (SENA)
unnamed: RSENB1.1, U1.6 (SENB)

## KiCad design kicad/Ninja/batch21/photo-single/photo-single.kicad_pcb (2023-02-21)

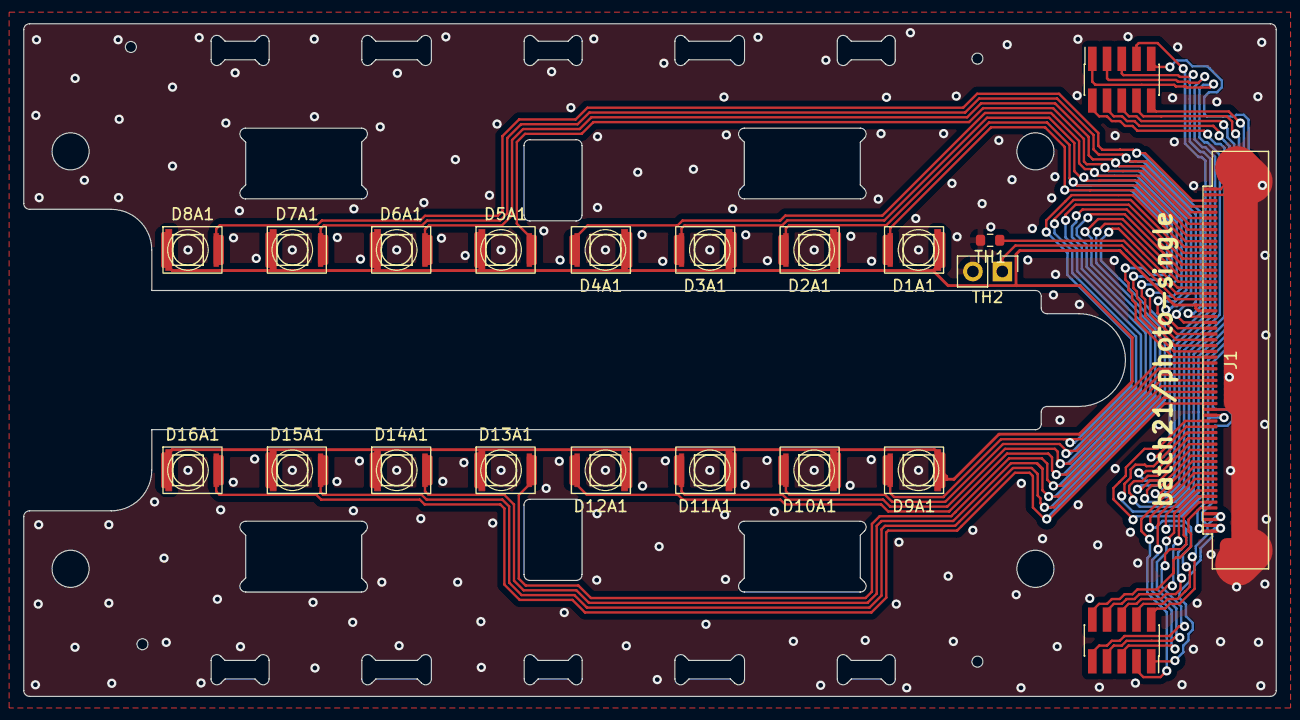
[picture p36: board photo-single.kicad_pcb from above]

Board: 2 copper layers, 108.0 x 58.0 mm, 21 parts (0 on the bottom side), 38 nets.

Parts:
D1A1, D2A1, D3A1, D4A1, D5A1, D6A1, D7A1, D8A1, D9A1, D10A1, D11A1, D12A1, D13A1, D14A1, D15A1, D16A1: D_Photo; SFH2200_2201_2240
J1: Conn_01x60_Male; FFC_60_Ali_HUISHUNFA
JLN1: Conn_01x10_Male; PinSocket_2x05_P1.27mm_Vertical_SMD
JLS1: Conn_01x10_Male; PinSocket_2x05_P1.27mm_Vertical_SMD
TH1: Thermistor; R_0603_1608Metric
TH2: Thermistor; PinHeader_1x02_P2.54mm_Vertical

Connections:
/N_LED_OUT1: J1.20, JLN1.8
/N_LED_OUT2: J1.19, JLN1.7
/N_LED_OUT3: J1.18, JLN1.6
/N_LED_OUT4: J1.17, JLN1.5
/N_LED_OUT5: J1.16, JLN1.4
/N_LED_OUT6: J1.15, JLN1.3
/N_LED_OUT7: J1.14, JLN1.2
/N_LED_OUT8: J1.13, JLN1.1
/N_PD_OUT1: D1A1.2 (A), J1.31, J1.51
/N_PD_OUT3: D2A1.2 (A), J1.32, J1.52
/N_PD_OUT5: D3A1.2 (A), J1.33, J1.53
/N_PD_OUT7: D4A1.2 (A), J1.34, J1.54
/N_PD_OUT9: D5A1.2 (A), J1.35, J1.55
/N_PD_OUT11: D6A1.2 (A), J1.36, J1.56
/N_PD_OUT13: D7A1.2 (A), J1.37, J1.57
/N_PD_OUT15: D8A1.2 (A), J1.38, J1.58
/S_LED_OUT1: J1.12, JLS1.3
/S_LED_OUT2: J1.11, JLS1.4
/S_LED_OUT3: J1.10, JLS1.5
/S_LED_OUT4: J1.9, JLS1.6
/S_LED_OUT5: J1.8, JLS1.7
/S_LED_OUT6: J1.7, JLS1.8
/S_LED_OUT7: J1.6, JLS1.9
/S_LED_OUT8: J1.5, JLS1.10
/S_PD_OUT1: D9A1.2 (A), J1.30, J1.50
/S_PD_OUT3: D10A1.2 (A), J1.29, J1.49
/S_PD_OUT5: D11A1.2 (A), J1.28, J1.48
/S_PD_OUT7: D12A1.2 (A), J1.27, J1.47
/S_PD_OUT9: D13A1.2 (A), J1.26, J1.46
/S_PD_OUT11: D14A1.2 (A), J1.25, J1.45
/S_PD_OUT13: D15A1.2 (A), J1.24, J1.44
/S_PD_OUT15: D16A1.2 (A), J1.23, J1.43
GNDA: J1.22, J1.59, J1.60, J1.G1, J1.G2, TH1.2, TH2.2
GNDL: J1.1, J1.2, J1.21, JLN1.10, JLS1.1
unnamed: J1.41, TH2.1
unnamed: J1.42, TH1.1
VCCA: D1A1.1 (K), D2A1.1 (K), D3A1.1 (K), D4A1.1 (K), D5A1.1 (K), D6A1.1 (K), D7A1.1 (K), D8A1.1 (K), D9A1.1 (K), D10A1.1 (K), D11A1.1 (K), D12A1.1 (K), D13A1.1 (K), D14A1.1 (K), D15A1.1 (K), D16A1.1 (K), J1.39, J1.40
VCCL: J1.3, J1.4, JLN1.9, JLS1.2

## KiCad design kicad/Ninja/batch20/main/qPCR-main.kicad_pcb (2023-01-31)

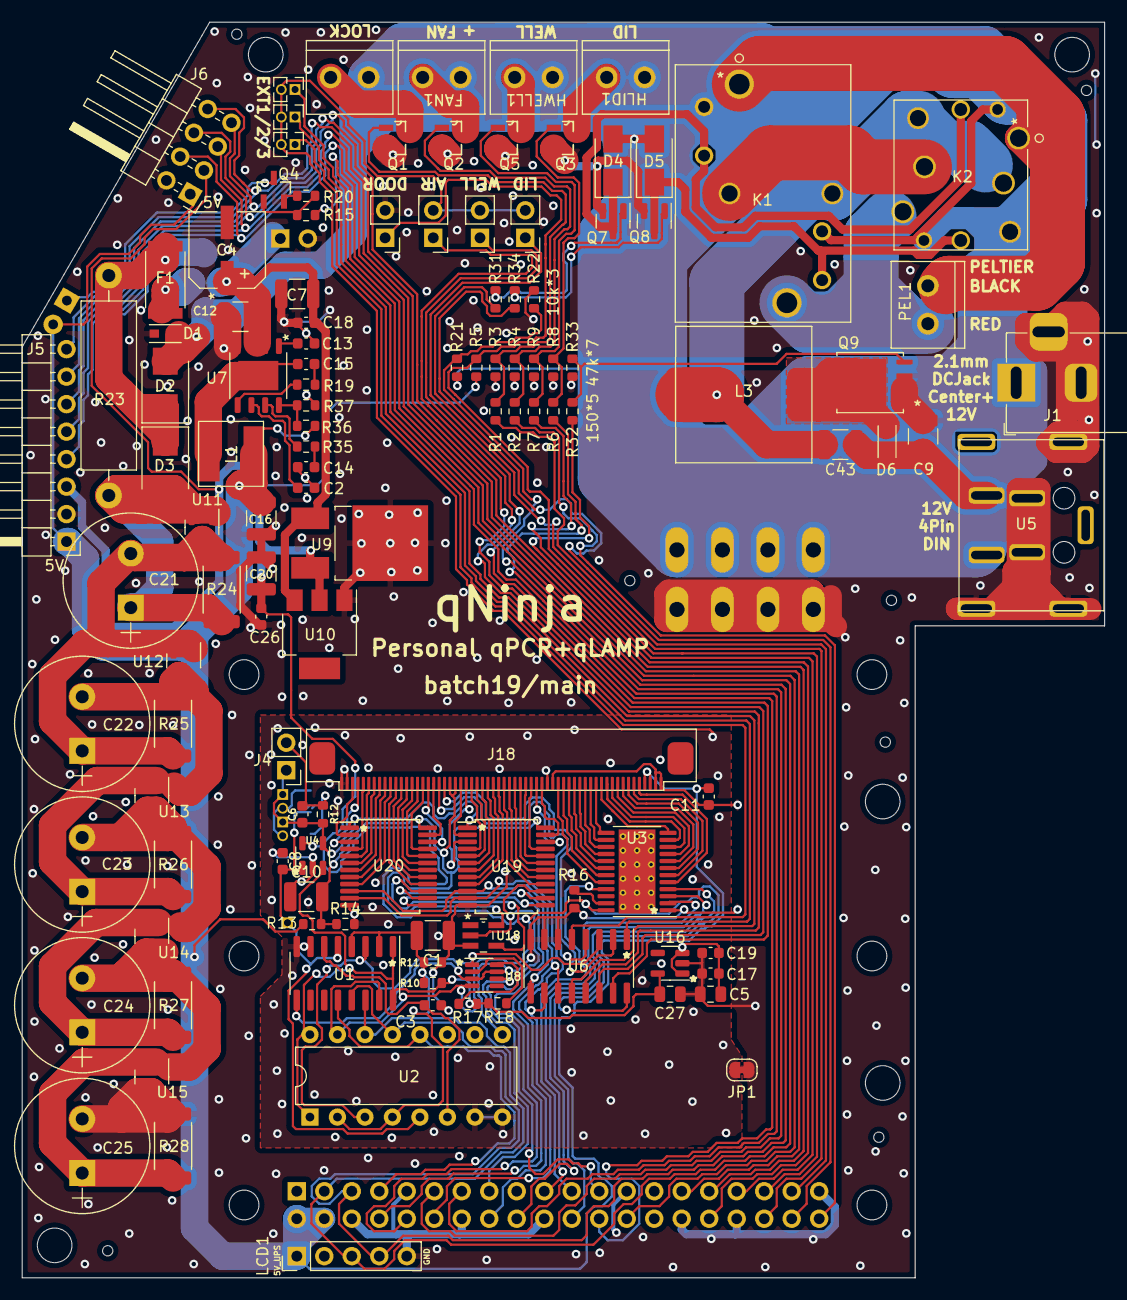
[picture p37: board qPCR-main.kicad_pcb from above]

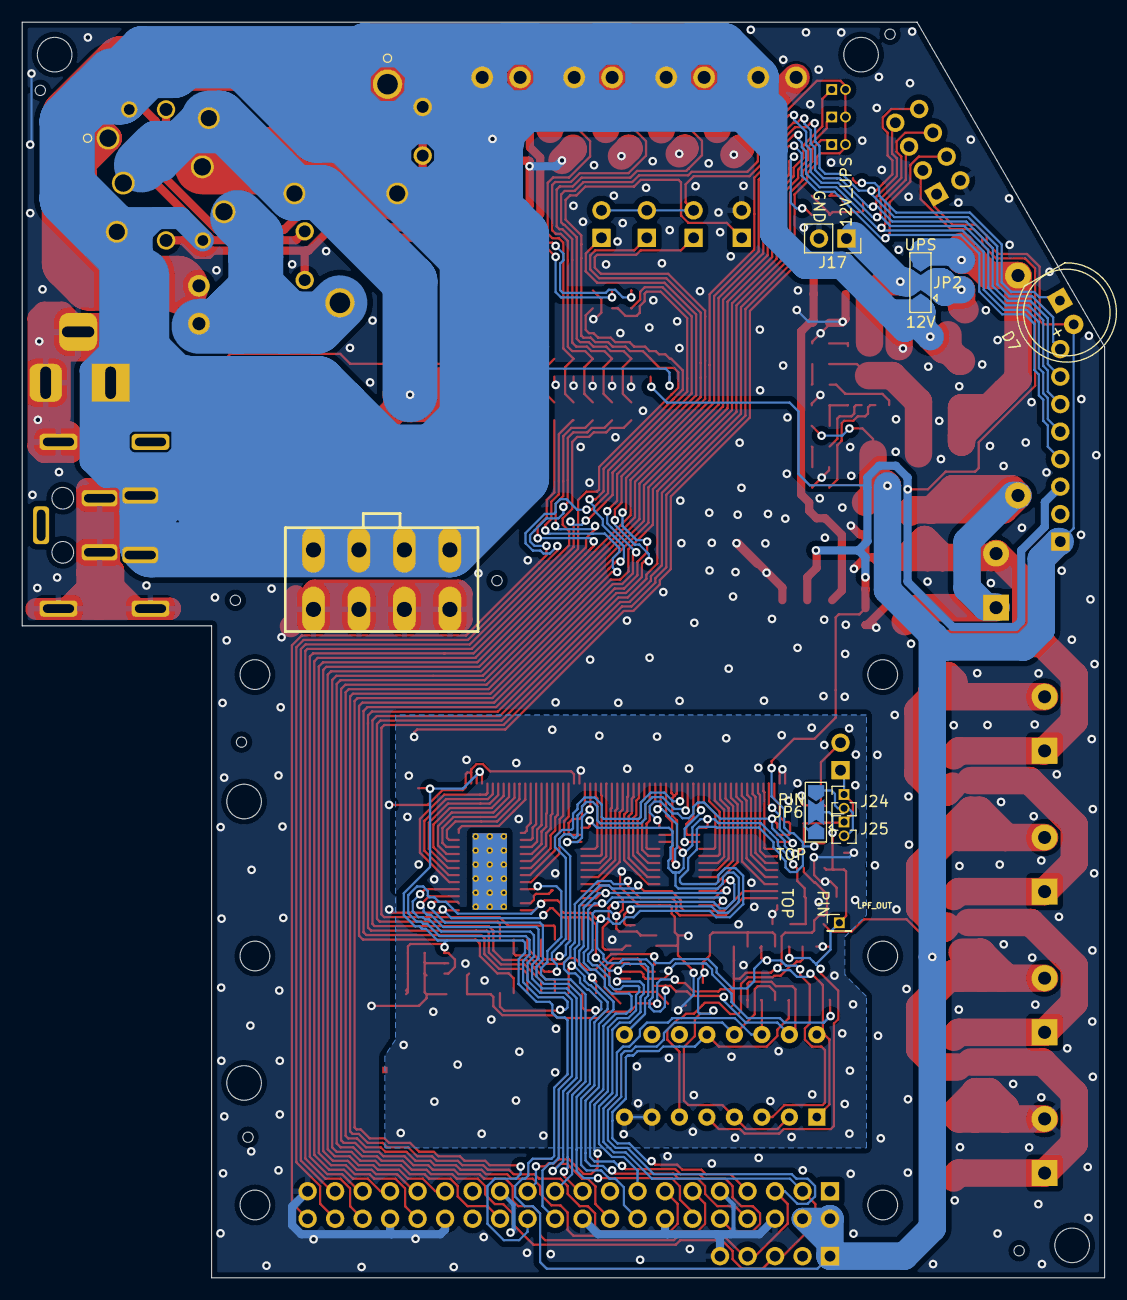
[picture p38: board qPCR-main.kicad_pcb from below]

Board: 2 copper layers, 100.0 x 116.0 mm, 129 parts (8 on the bottom side), 134 nets.

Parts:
C1, C7, C9, C10, C12, C16, C20, C43: 22uF; C_1210_3225Metric
C2, C3, C8, C11, C13, C17, C18, C26: 0.1uF; C_0603_1608Metric
C4: 100uF; 35TZV100M6.3X8
C5, C27: 4.7uF; C_0805_2012Metric
C6: 5pF; C_0603_1608Metric
C14, C15, C19: 0.01uF; C_0603_1608Metric
C21, C22, C23, C24, C25: 10F2.7V; CP_Radial_D12.5mm_P5.00mm
D1, D6: D_Schottky; MSS1P3L-M3&slash_89A
D2, D3: D; D_SMB
D4, D5: DIODE; D_SMA
D7: LED; LED_D8.0mm
F1: Fuse; R_2512
FAN1: Screw_Terminal_01x02; TB_SeeedOPL_320110028
HLID1: Screw_Terminal_01x02; TB_SeeedOPL_320110028
HWELL1: Screw_Terminal_01x02; TB_SeeedOPL_320110028
J1: Barrel_Jack_Switch; BarrelJack_Horizontal
J2: Raspberry_Pi_3A_Plus_wpi; Raspberry_Pi_3A+_3B+_4B_Zero_FaceDown_HDMI-R-NOSILK
J3: Conn_01x08_Male; ATX8
J4: Conn_01x02_Male; PinHeader_1x02_P2.54mm_Vertical
J5: Conn_01x08_Male; PinHeader_1x08_P2.54mm_Horizontal
J6: Conn_01x08_Male; PinHeader_2x04_P2.54mm_Horizontal
J17: Conn_01x02_Male; PinSocket_1x02_P2.54mm_Vertical
J18: Conn_01x60_Male; FFC_60_Ali_HUISHUNFA
J23: Conn_01x01_Male; PinHeader_1x01_P1.27mm_Vertical
J24, J25: Conn_01x02_Male; PinHeader_1x02_P1.27mm_Vertical
JP1: SolderJumper_2_Bridged; SolderJumper-2_P1.3mm_Bridged_RoundedPad1.0x1.5mm
JP2, JP6: Jumper_3_Open; SolderJumper-3_P2.0mm_Open_TrianglePad1.0x1.5mm
K1: EP2-3L3SAb
K2: EX2-2U1S
L1: 10uH; VLS6045EX-3R3N
L3: SRP1265C-220M; SRP1265C
LCD1: RPI_LCD_TOUCH_7INCH; PinHeader_1x05_P2.54mm_Vertical
LOCK1: Conn_01x02_Male; TB_SeeedOPL_320110028
PEL1: Screw_Terminal_01x02; TB_SeeedOPL_320110028
Q1, Q2, Q3, Q4, Q5: Q_NMOS_GSD; SOT95P240X112-3N
Q7, Q8: Q_NPN_BCE; SOT-23
Q9: SIRA88BDP-T1-GE3; PowerPAK_SO-8_Long
R1, R2, R6, R7, R15, R19, R32: 150; R_0603_1608Metric
R3, R4, R5, R8, R9, R20, R21, R33: 47k; R_0603_1608Metric
R10, R11, R18: 47k_HP; R_0603_1608Metric
R12: 10M; R_0603_1608Metric
R13, R22, R31, R34, R35, R37: 10k; R_0603_1608Metric
R14: 100k; R_0603_1608Metric
R16: 3.3k; R_0603_1608Metric
R17: 10k_HP; R_0603_1608Metric
R23: 8.2Ω 3W; R_Axial_DIN0516_L15.5mm_D5.0mm_P20.32mm_Horizontal
R24, R25, R26, R27, R28: 1k2W; R_2512_6332Metric
R36: 75k; R_0603_1608Metric
SW1: SW_Reed; PinHeader_1x02_P2.54mm_Vertical
TAIR1: Conn_01x02_Male; PinHeader_1x02_P2.54mm_Vertical
TEXT1, TEXT2, TEXT3: Conn_01x02_Male; PinHeader_1x02_P1.27mm_Vertical
TLID1: Conn_01x02_Male; PinHeader_1x02_P2.54mm_Vertical
TWELL1: Conn_01x02_Male; PinHeader_1x02_P2.54mm_Vertical
U1: NAU7802; SOIC-16_3.9x9.9mm_P1.27mm
U2: NAU7802; DIP-16_W7.62mm
U3: TLC5929; HTSSOP-24-1EP_4.4x7.8mm_P0.65mm_EP3.4x7.8mm_Mask2.4x4.68mm_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
U4: LMP7717MF_NOPB; SOT-23-5
U5: DIN4_PWR; DN4_PWR
U6: SN74LV4051A; SOIC-16_3.9x9.9mm_P1.27mm
U7: AOZ6600; AOZ6605PI-1
U8: TS12A12511DCNR; SOT-23-8-8.3mil
U9: REG_TO252-3
U10: LD1086DTTR; SOT-223
U11, U12, U13, U14, U15: TL431DBZ; SOT-23
U16: MCP1755T-3302E_OT; SOT-23-5
U18: SN74LVC1GU04DCKR; SN74LVC1GU04DBVR
U19, U20: CD74HC4067M96; SSOP-24_5.3x8.2mm_P0.65mm-0.83mil

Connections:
3V3A: C27.1, R10.1, R17.1, R18.1, U1.1 (REFP), U1.16 (AVDD), U2.1 (REFP), U2.16 (AVDD), U4.3 (IN+), U16.5 (VOUT)
3V3D: C20.1, C26.1, J5.3, J6.3, R5.1, U1.15 (DVDD), U2.15 (DVDD), U3.24 (VCC), U4.5 (V+), U6.16 (VCC), U8.4 (V+), U9.2 (VOUT), U10.2 (OUT)
5V_UPS: C5.1, C11.1, C16.2, C17.1, C19.1, D7.2 (A), J2.2 (5V), J2.4 (5V), J5.1, J6.1, J18.3, J18.4, L1.1, LCD1.1 (5V), R13.1, R36.1, U16.1 (VIN), U16.3 (SHDN)
12V: C9.1, C43.1, D1.1 (K), D2.2 (A), D4.2 (A), D5.2 (A), D6.1 (K), FAN1.1, HLID1.1, HWELL1.1, J1.1, J3.5, J3.6, J3.7, J3.8, JP2.1 (A), K1.2, K1.4, K1.6, K2.2, K2.5, K2.7, K2.9, LOCK1.1, R21.1, U5.1 (VIN1), U5.2 (VIN2)
12V_UPS: C4.1, C7.1, C12.2, C18.1, F1.1, J17.1, JP2.2 (C), U7.2 (EN), U7.3 (VIN), U9.1 (VIN), U10.3 (IN)
/FAN: J2.40 (GPIO29), R2.2
/LID_HEATER: J2.13 (GPIO2), R6.2
/Photo/AMP_OUT: C8.1, J23.1, JP6.2 (C), U1.5 (VIN2P), U2.5 (VIN2P), U4.1 (OUT)
/Photo/VBG: C3.1, U1.6 (VBG), U2.6 (VBG)
/PhotoMUX/MUX_SELECT_INV: U18.4, U20.15 (*E)
/PhotoMUX/N_PD_OUT1: J18.31, U19.9 (I0)
/PhotoMUX/N_PD_OUT2: J18.51, U20.9 (I0)
/PhotoMUX/N_PD_OUT3: J18.32, U19.8 (I1)
/PhotoMUX/N_PD_OUT4: J18.52, U20.8 (I1)
/PhotoMUX/N_PD_OUT5: J18.33, U19.7 (I2)
/PhotoMUX/N_PD_OUT6: J18.53, U20.7 (I2)
/PhotoMUX/N_PD_OUT7: J18.34, U19.6 (I3)
/PhotoMUX/N_PD_OUT8: J18.54, U20.6 (I3)
/PhotoMUX/N_PD_OUT9: J18.35, U19.5 (I4)
/PhotoMUX/N_PD_OUT10: J18.55, U20.5 (I4)
/PhotoMUX/N_PD_OUT11: J18.36, U19.4 (I5)
/PhotoMUX/N_PD_OUT12: J18.56, U20.4 (I5)
/PhotoMUX/N_PD_OUT13: J18.37, U19.3 (I6)
/PhotoMUX/N_PD_OUT14: J18.57, U20.3 (I6)
/PhotoMUX/N_PD_OUT15: J18.38, U19.2 (I7)
/PhotoMUX/N_PD_OUT16: J18.58, U20.2 (I7)
/PhotoMUX/S_PD_OUT1: J18.30, U19.16 (I15)
/PhotoMUX/S_PD_OUT2: J18.50, U20.16 (I15)
/PhotoMUX/S_PD_OUT3: J18.29, U19.17 (I14)
/PhotoMUX/S_PD_OUT4: J18.49, U20.17 (I14)
/PhotoMUX/S_PD_OUT5: J18.28, U19.18 (I13)
/PhotoMUX/S_PD_OUT6: J18.48, U20.18 (I13)
/PhotoMUX/S_PD_OUT7: J18.27, U19.19 (I12)
/PhotoMUX/S_PD_OUT8: J18.47, U20.19 (I12)
/PhotoMUX/S_PD_OUT9: J18.26, U19.20 (I11)
/PhotoMUX/S_PD_OUT10: J18.46, U20.20 (I11)
/PhotoMUX/S_PD_OUT11: J18.25, U19.21 (I10)
/PhotoMUX/S_PD_OUT12: J18.45, U20.21 (I10)
/PhotoMUX/S_PD_OUT13: J18.24, U19.22 (I9)
/PhotoMUX/S_PD_OUT14: J18.44, U20.22 (I9)
/PhotoMUX/S_PD_OUT15: J18.23, U19.23 (I8)
/PhotoMUX/S_PD_OUT16: J18.43, U20.23 (I8)
/Power/5V_SW: C15.2, L1.2, U7.EP (LX)
/SheetPeltier/PEL1: D4.1 (K), K1.3, K2.3, Q7.3 (C)
/SheetPeltier/PEL3: D5.1 (K), K1.7, K2.8, Q8.3 (C)
/SheetPeltier/PEL_BLK: K1.1, K2.1, PEL1.2
/SheetPeltier/PEL_RED: K1.8, K2.6, PEL1.1
/SheetPeltier/REG_D: D6.2 (A), L3.1, Q9.5 (D)
/WELL_HEATER: J2.33 (GPIO23/PWM1), R7.2
DIVIDED: C1.2, R10.2, R11.1, U1.2 (VIN1N), U1.4 (VIN2N), U2.2 (VIN1N), U2.4 (VIN2N)
DLOCK: J2.37 (GPIO25), R1.2
DOPEN: J2.35 (GPIO24), R5.2, SW1.1
GNDA: C1.1, C3.2, C8.2, C10.1, J18.22, J18.59, J18.60, JP1.2 (B), R11.2, R14.2, TAIR1.2, TEXT1.2, TEXT2.2, TEXT3.2, TLID1.2, TWELL1.2, U1.7 (REFN), U1.8 (AVSS), U2.7 (REFN), U2.8 (AVSS), U4.2 (V-), U18.3, U19.12 (GND), U20.12 (GND)
GNDD: C2.1, C4.2, C5.2, C7.2, C9.2, C11.2, C12.1, C13.1, C14.1, C16.1, C17.2, C18.2, C19.2, C20.2, C25.2, C26.2, C27.2, D1.2 (A), J1.2, J1.3, J2.6 (GND), J2.9 (GND), J2.14 (GND), J2.20 (GND), J2.25 (GND), J2.30 (GND), J2.34 (GND), J2.39 (GND), J3.1, J3.2, J3.3, J3.4, J5.2, J6.2, J17.2, J18.1, J18.2, J18.21, JP1.1 (A), LCD1.5 (GND), Q1.2 (S), Q2.2 (S), Q3.2 (S), Q4.2 (S), Q5.2 (S), Q7.2 (E), Q8.2 (E), Q9.1 (S), Q9.2 (S), Q9.3 (S), R3.1, R4.1, R8.1, R9.1, R16.1, R20.1, R22.2, R28.1, R33.2, R37.2, SW1.2, U1.9 (DVSS), U2.9 (DVSS), U3.1 (GND), U5.3 (GND), U5.4 (GND), U5.6 (CASE), U5.7 (CASE), U5.9 (CASE), U6.6 (INH), U6.7 (GND), U6.8 (GND), U7.4 (GND), U8.3 (GND), U8.7 (V-), U9.3 (GND), U10.1 (ADJ/GND), U15.3 (A), U16.2 (GND)
I2C_SCL: J2.5 (GPIO9/SCL1), J5.4, J6.4, LCD1.4 (SCL), U1.13 (SCLK), U2.13 (SCLK)
I2C_SDA: J2.3 (GPIO8/SDA1), J5.5, J6.5, LCD1.3 (SDA), U1.14 (SDIO), U2.14 (SDIO)
LED: J2.24 (GPIO10/CE0), R15.2
LED_BLANK: J2.21 (GPIO13/MISO), U3.21 (BLANK)
LED_C: D7.1 (K), Q4.3 (D)
LED_LAT: J2.22 (GPIO6), U3.4 (LAT)
LED_SPI_MOSI: J2.19 (GPIO12/MOSI), U3.2 (SIN)
LED_SPI_SCLK: J2.18 (GPIO5), U3.3 (SCLK)
MUX_S0: J2.16 (GPIO4), U6.11 (A), U19.10 (S0), U20.10 (S0)
MUX_S1: J2.12 (GPIO1/PWM0), U6.10 (B), U19.11 (S1), U20.11 (S1)
MUX_S2: J2.8 (GPIO15/TXD), U6.9 (C), U19.14 (S2), U20.14 (S2)
MUX_S3: J2.10 (GPIO16/RXD), U19.13 (S3), U20.13 (S3)
MUX_SELECT: J2.23 (GPIO14/SCLK), U18.2, U19.15 (*E)
NAU_DRDY: J2.7 (GPIO7), U1.12 (DRDY), U2.12 (DRDY)
N_LED_OUT1: J18.20, U3.20 (OUT15)
N_LED_OUT2: J18.19, U3.19 (OUT14)
N_LED_OUT3: J18.18, U3.18 (OUT13)
N_LED_OUT4: J18.17, U3.17 (OUT12)
N_LED_OUT5: J18.16, U3.16 (OUT11)
N_LED_OUT6: J18.15, U3.15 (OUT10)
N_LED_OUT7: J18.14, U3.14 (OUT9)
N_LED_OUT8: J18.13, U3.13 (OUT8)
unnamed: C2.2, U7.6 (VCC)
unnamed: C6.1, J4.2, JP6.1 (A), R12.2
unnamed: C13.2, U7.1 (SS)
unnamed: C14.2, R35.2
unnamed: C15.1, R19.2
unnamed: C21.1, D3.2 (A), R23.1, R24.2, U11.1 (K), U11.2 (REF)
unnamed: C21.2, C22.1, R24.1, R25.2, U11.3 (A), U12.1 (K), U12.2 (REF)
unnamed: C22.2, C23.1, R25.1, R26.2, U12.3 (A), U13.1 (K), U13.2 (REF)
unnamed: C23.2, C24.1, R26.1, R27.2, U13.3 (A), U14.1 (K), U14.2 (REF)
unnamed: C24.2, C25.1, R27.1, R28.2, U14.3 (A), U15.1 (K), U15.2 (REF)
unnamed: D2.1 (K), D3.1 (K), F1.2, JP2.3 (B), R23.2
unnamed: FAN1.2, Q2.3 (D)
unnamed: HLID1.2, Q3.3 (D)
unnamed: HWELL1.2, Q5.3 (D)
unnamed: J24.2, J25.2, JP6.3 (B)
unnamed: LOCK1.2, Q1.3 (D)
unnamed: Q1.1 (G), R1.1, R3.2
unnamed: Q2.1 (G), R2.1, R4.2
unnamed: Q3.1 (G), R6.1, R8.2
unnamed: Q4.1 (G), R15.1, R20.2
unnamed: Q5.1 (G), R7.1, R9.2
unnamed: Q7.1 (B), R31.1
unnamed: Q8.1 (B), R34.2
unnamed: Q9.4 (G), R32.1, R33.1
unnamed: R16.2, U3.23 (IREF)
unnamed: R17.2, U8.8 (NO)
unnamed: R18.2, U8.2 (NC)
unnamed: R19.1, U7.5 (BST)
unnamed: R35.1, U7.7 (COMP)
unnamed: R36.2, R37.1, U7.8 (FB)
PD_MUX_OUT: C6.2, J4.1, J24.1, J25.1, R12.1, U4.4 (IN-), U19.1 (COMMONINPUT/OUTPUT), U20.1 (COMMONINPUT/OUTPUT)
PD_TH1: J18.41, U6.2 (Y6)
PD_TH2: J18.42, U6.4 (Y7)
PEL_PWM: J2.32 (GPIO26/PWM0), R32.2
PEL_SWA: J2.36 (GPIO27), R31.2
PEL_SWB: J2.38 (GPIO28), R34.1
REG_OUT: C43.2, K1.5, K2.4, K2.10, L3.2
S_LED_OUT1: J18.12, U3.12 (OUT7)
S_LED_OUT2: J18.11, U3.11 (OUT6)
S_LED_OUT3: J18.10, U3.10 (OUT5)
S_LED_OUT4: J18.9, U3.9 (OUT4)
S_LED_OUT5: J18.8, U3.8 (OUT3)
S_LED_OUT6: J18.7, U3.7 (OUT2)
S_LED_OUT7: J18.6, U3.6 (OUT1)
S_LED_OUT8: J18.5, U3.5 (OUT0)
TACT1: J2.26 (GPIO11/CE1), J5.8, J6.8
TACT2: J2.29 (GPIO21), J5.7, J6.7
TACT3: J2.31 (GPIO22), J5.6, J6.6
THERM_AIR: TAIR1.1, U6.14 (Y1)
THERM_EXT1: TEXT1.1, U6.12 (Y3)
THERM_EXT2: TEXT2.1, U6.1 (Y4)
THERM_EXT3: TEXT3.1, U6.5 (Y5)
THERM_LID: TLID1.1, U6.15 (Y2)
THERM_MUX_OUT: U1.3 (VIN1P), U2.3 (VIN1P), U6.3 (COM), U8.1 (COM)
THERM_R_SWITCH: J2.15 (GPIO3), U8.6 (IN)
THERM_WELL: TWELL1.1, U6.13 (Y0)
VIN_SENSE: J2.11 (GPIO0), R21.2, R22.1
VOPT: C10.2, J18.39, J18.40, R13.2, R14.1, U18.5, U19.24 (VCC), U20.24 (VCC)

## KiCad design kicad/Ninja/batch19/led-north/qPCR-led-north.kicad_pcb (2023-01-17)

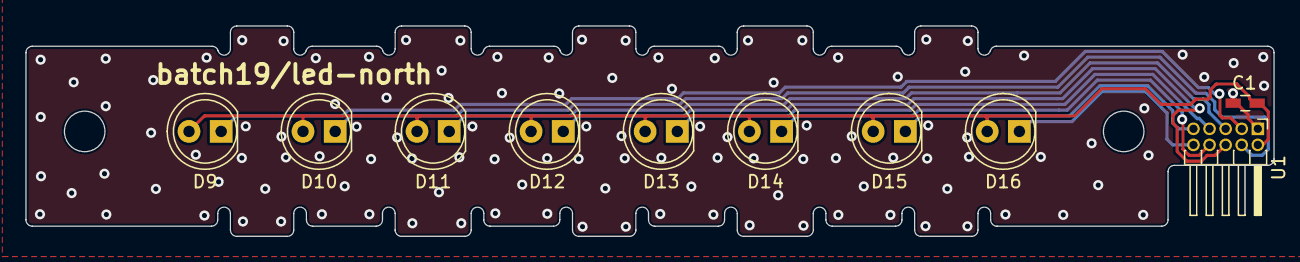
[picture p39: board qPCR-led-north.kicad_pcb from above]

Board: 2 copper layers, 98.5 x 16.6 mm, 10 parts (0 on the bottom side), 10 nets.

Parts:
C1: C; C_0603_HandSoldering
D9, D10, D11, D12, D13, D14, D15, D16: LED; LED_D5.0mm
U1: Conn_01x10_Male; PinHeader_2x05_P1.27mm_Horizontal

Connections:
GND: C1.2, U1.1
OUT9: D9.1 (K), U1.3
OUT10: D10.1 (K), U1.4
OUT11: D11.1 (K), U1.5
OUT12: D12.1 (K), U1.6
OUT13: D13.1 (K), U1.7
OUT14: D14.1 (K), U1.8
OUT15: D15.1 (K), U1.9
OUT16: D16.1 (K), U1.10
VCC: C1.1, D9.2 (A), D10.2 (A), D11.2 (A), D12.2 (A), D13.2 (A), D14.2 (A), D15.2 (A), D16.2 (A), U1.2

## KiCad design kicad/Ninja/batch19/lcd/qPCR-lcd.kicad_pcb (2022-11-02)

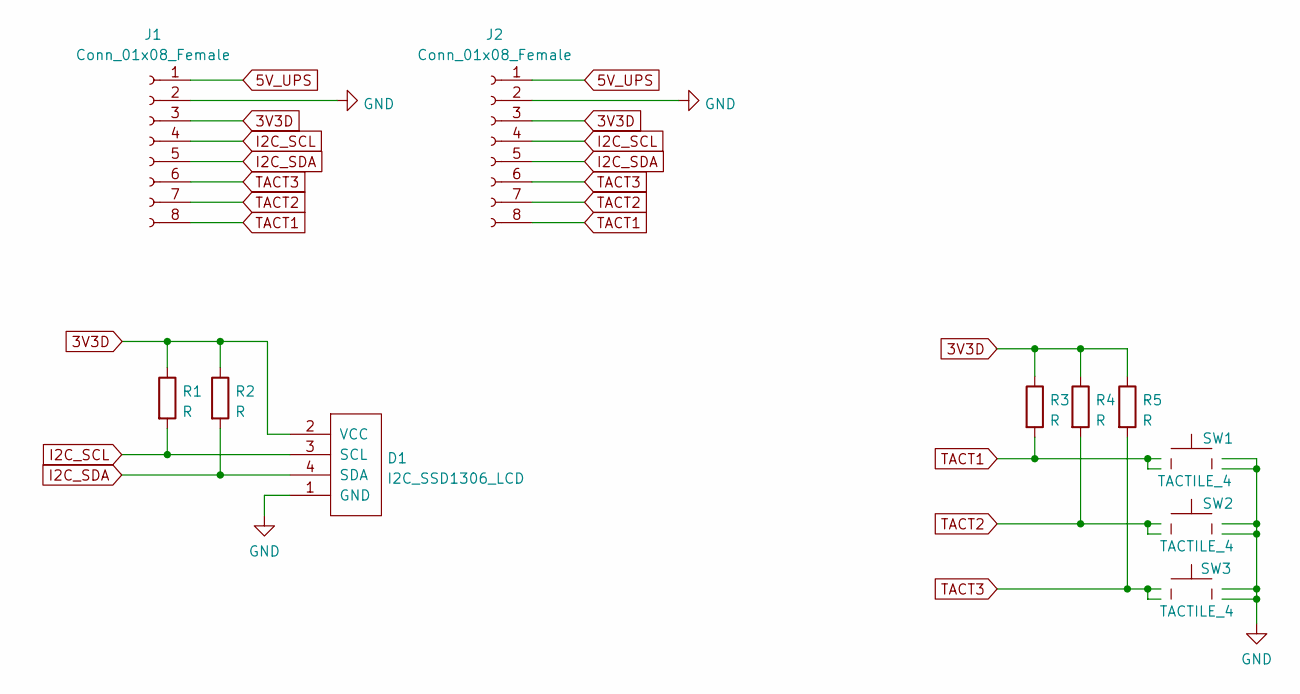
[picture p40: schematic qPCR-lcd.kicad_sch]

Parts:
D1: I2C_SSD1306_LCD; ALI_I2C_LCD
J1: Conn_01x08_Female; PinSocket_1x08_P2.54mm_Vertical
J2: Conn_01x08_Female; PinSocket_2x04_P2.54mm_Vertical
R1, R2, R3, R4, R5: R; R_0603_1608Metric
SW1, SW2, SW3: TACTILE_4; SW_TH_Tactile_Omron_B3F-10xx

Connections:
3V3D: D1.2 (VCC), J1.3, J2.3, R1.1, R2.1, R3.1, R4.1, R5.1
5V_UPS: J1.1, J2.1
GND: D1.1 (GND), J1.2, J2.2, SW1.3, SW1.4, SW2.3, SW2.4, SW3.3, SW3.4
I2C_SCL: D1.3 (SCL), J1.4, J2.4, R1.2
I2C_SDA: D1.4 (SDA), J1.5, J2.5, R2.2
TACT1: J1.8, J2.8, R3.2, SW1.1, SW1.2
TACT2: J1.7, J2.7, R4.2, SW2.1, SW2.2
TACT3: J1.6, J2.6, R5.2, SW3.1, SW3.2

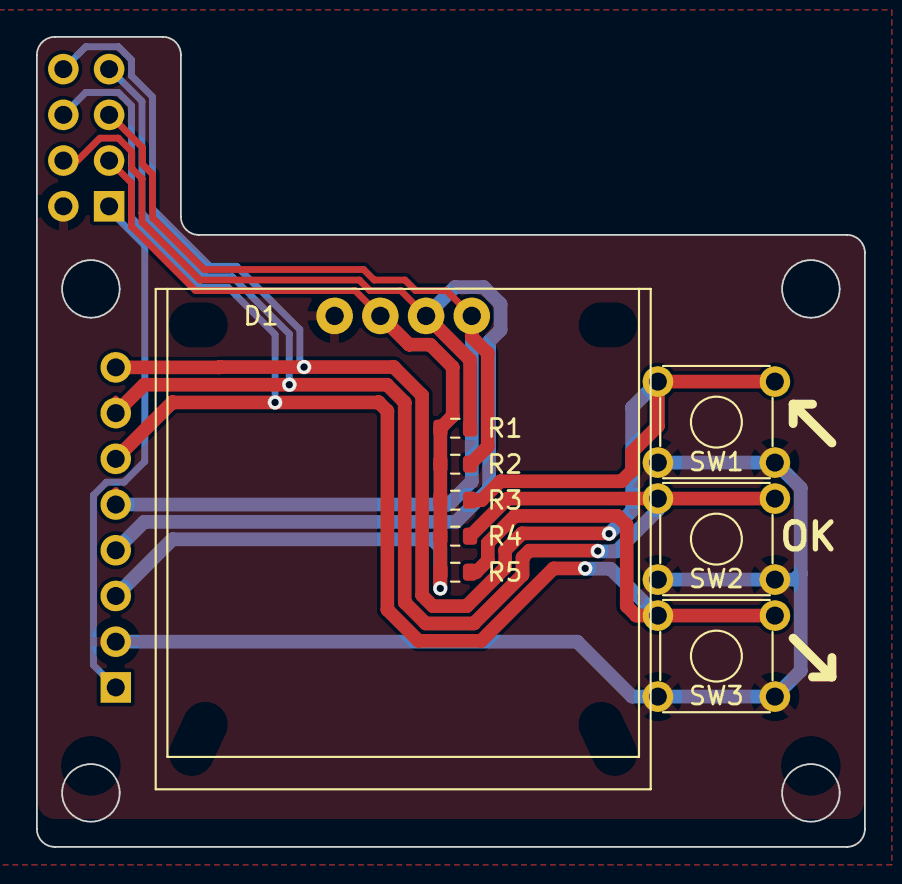
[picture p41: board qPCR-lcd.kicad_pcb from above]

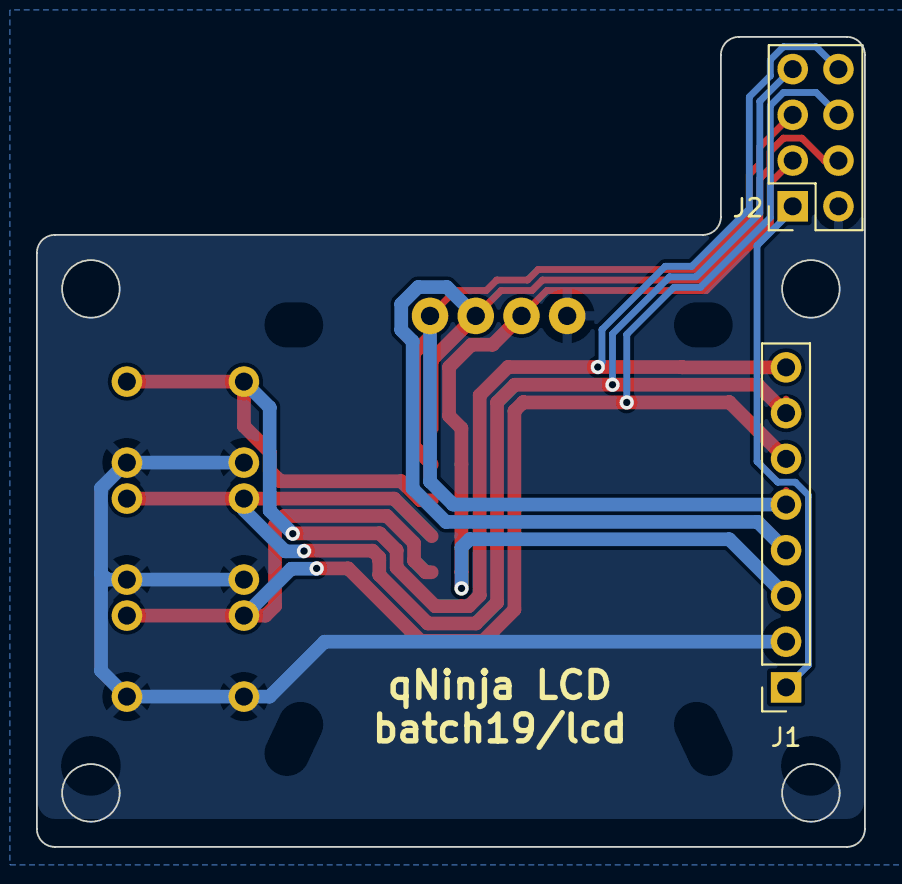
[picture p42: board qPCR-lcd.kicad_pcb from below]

Board: 2 copper layers, 46.0 x 45.0 mm, 11 parts (2 on the bottom side), 8 nets.

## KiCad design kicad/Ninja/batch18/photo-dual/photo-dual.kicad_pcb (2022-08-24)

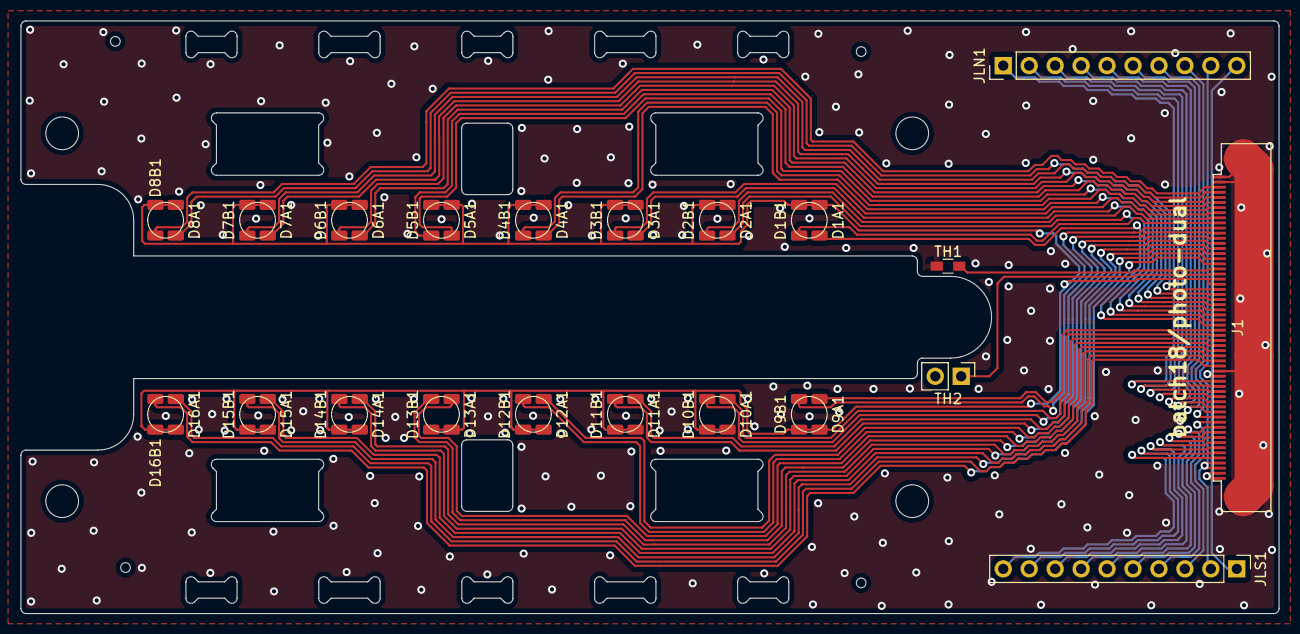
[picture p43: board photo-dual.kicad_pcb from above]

Board: 2 copper layers, 123.1 x 58.0 mm, 37 parts (0 on the bottom side), 54 nets.

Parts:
D1A1, D1B1, D2A1, D2B1, D3A1, D3B1, D4A1, D4B1, D5A1, D5B1, D6A1, D6B1, D7A1, D7B1, D8A1, D8B1, D9A1, D9B1, D10A1, D10B1, D11A1, D11B1, D12A1, D12B1, D13A1, D13B1, D14A1, D14B1, D15A1, D15B1, D16A1, D16B1: D_Photo; D_1206_nosilk
J1: Conn_01x60_Male; FFC_60_Ali_HUISHUNFA
JLN1: Conn_01x10_Male; Pin_Header_Straight_1x10_Pitch2.54mm
JLS1: Conn_01x10_Male; Pin_Header_Straight_1x10_Pitch2.54mm
TH1: Thermistor; R_0603_HandSoldering
TH2: Thermistor; PinHeader_1x02_P2.54mm_Vertical

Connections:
/N_LED_OUT1: J1.20, JLN1.1
/N_LED_OUT2: J1.19, JLN1.2
/N_LED_OUT3: J1.18, JLN1.3
/N_LED_OUT4: J1.17, JLN1.4
/N_LED_OUT5: J1.16, JLN1.5
/N_LED_OUT6: J1.15, JLN1.6
/N_LED_OUT7: J1.14, JLN1.7
/N_LED_OUT8: J1.13, JLN1.8
/N_PD_OUT1: D1A1.2 (A), J1.31
/N_PD_OUT2: D1B1.2 (A), J1.51
/N_PD_OUT3: D2A1.2 (A), J1.32
/N_PD_OUT4: D2B1.2 (A), J1.52
/N_PD_OUT5: D3A1.2 (A), J1.33
/N_PD_OUT6: D3B1.2 (A), J1.53
/N_PD_OUT7: D4A1.2 (A), J1.34
/N_PD_OUT8: D4B1.2 (A), J1.54
/N_PD_OUT9: D5A1.2 (A), J1.35
/N_PD_OUT10: D5B1.2 (A), J1.55
/N_PD_OUT11: D6A1.2 (A), J1.36
/N_PD_OUT12: D6B1.2 (A), J1.56
/N_PD_OUT13: D7A1.2 (A), J1.37
/N_PD_OUT14: D7B1.2 (A), J1.57
/N_PD_OUT15: D8A1.2 (A), J1.38
/N_PD_OUT16: D8B1.2 (A), J1.58
/S_LED_OUT1: J1.12, JLS1.3
/S_LED_OUT2: J1.11, JLS1.4
/S_LED_OUT3: J1.10, JLS1.5
/S_LED_OUT4: J1.9, JLS1.6
/S_LED_OUT5: J1.8, JLS1.7
/S_LED_OUT6: J1.7, JLS1.8
/S_LED_OUT7: J1.6, JLS1.9
/S_LED_OUT8: J1.5, JLS1.10
/S_PD_OUT1: D9A1.2 (A), J1.30
/S_PD_OUT2: D9B1.2 (A), J1.50
/S_PD_OUT3: D10A1.2 (A), J1.29
/S_PD_OUT4: D10B1.2 (A), J1.49
/S_PD_OUT5: D11A1.2 (A), J1.28
/S_PD_OUT6: D11B1.2 (A), J1.48
/S_PD_OUT7: D12A1.2 (A), J1.27
/S_PD_OUT8: D12B1.2 (A), J1.47
/S_PD_OUT9: D13A1.2 (A), J1.26
/S_PD_OUT10: D13B1.2 (A), J1.46
/S_PD_OUT11: D14A1.2 (A), J1.25
/S_PD_OUT12: D14B1.2 (A), J1.45
/S_PD_OUT13: D15A1.2 (A), J1.24
/S_PD_OUT14: D15B1.2 (A), J1.44
/S_PD_OUT15: D16A1.2 (A), J1.23
/S_PD_OUT16: D16B1.2 (A), J1.43
/TH1: J1.42, TH1.1
/TH2: J1.41, TH2.1
GNDA: J1.22, J1.59, J1.60, J1.G1, J1.G2, TH1.2, TH2.2
GNDL: J1.1, J1.2, J1.21, JLN1.10, JLS1.1
VCCA: D1A1.1 (K), D1B1.1 (K), D2A1.1 (K), D2B1.1 (K), D3A1.1 (K), D3B1.1 (K), D4A1.1 (K), D4B1.1 (K), D5A1.1 (K), D5B1.1 (K), D6A1.1 (K), D6B1.1 (K), D7A1.1 (K), D7B1.1 (K), D8A1.1 (K), D8B1.1 (K), D9A1.1 (K), D9B1.1 (K), D10A1.1 (K), D10B1.1 (K), D11A1.1 (K), D11B1.1 (K), D12A1.1 (K), D12B1.1 (K), D13A1.1 (K), D13B1.1 (K), D14A1.1 (K), D14B1.1 (K), D15A1.1 (K), D15B1.1 (K), D16A1.1 (K), D16B1.1 (K), J1.39, J1.40
VCCL: J1.3, J1.4, JLN1.9, JLS1.2

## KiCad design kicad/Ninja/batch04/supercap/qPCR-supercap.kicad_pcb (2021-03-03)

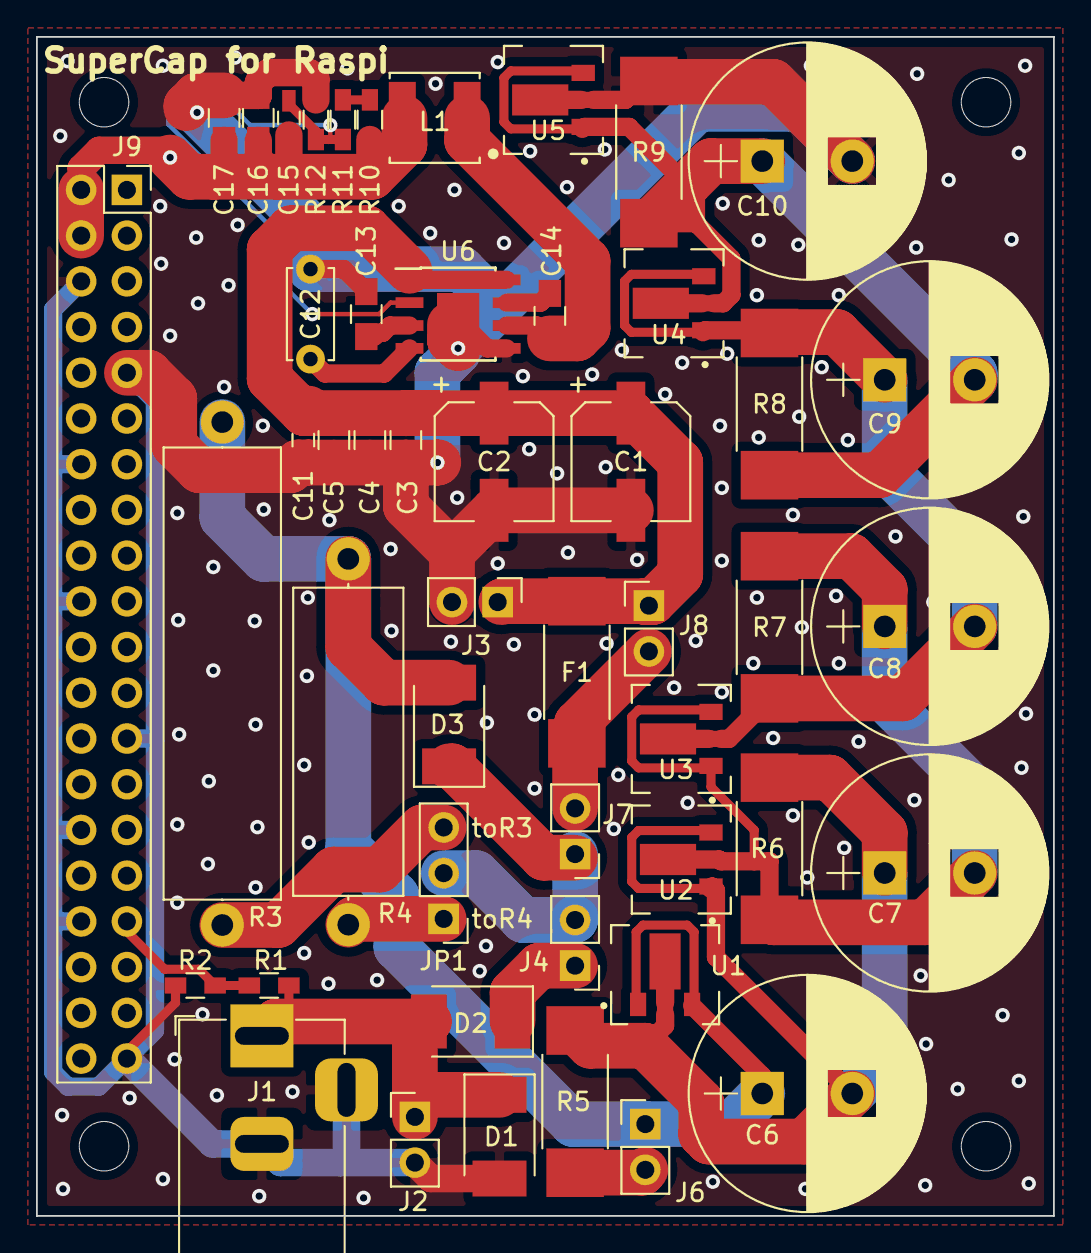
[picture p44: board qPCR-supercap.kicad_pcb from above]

Board: 2 copper layers, 56.5 x 65.5 mm, 49 parts (0 on the bottom side), 22 nets.

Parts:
C1, C2: 100uF; CP_Elec_6.3x5.8
C3, C4: 10uF; C_0805_HandSoldering
C5, C14: 0.1uF; C_0805_HandSoldering
C6, C7, C8, C9, C10: 10F2.7V; CP_Radial_D13.0mm_P5.00mm
C11: 0.01uF; C_0603_HandSoldering
C12: 3300pF; C_Disc_D5.0mm_W2.5mm_P5.00mm
C13: 1uF; C_0805_HandSoldering
C15: (5-100pF); C_0603_HandSoldering
C16, C17: 22uF; C_0805_HandSoldering
D1: D_Schottky; D_2114
D2, D3: D; D_2114
F1: Fuse; R_2512_HandSoldering
J1: Barrel_Jack_Switch; BarrelJack_Horizontal
J2, J3, J4, J6, J7, J8: Conn_01x02_Male; Pin_Header_Straight_1x02_Pitch2.54mm
J9: Raspberry_Pi_3A_Plus_wpi; Raspberry_Pi_3A+_Socketed_THT_FaceDown_MountingHoles_minimum
JP1: Jumper_3_Open; Pin_Header_Straight_1x03_Pitch2.54mm
L1: 3.3uH(ALPS GLMC / TDK SPM6530); IND_VLS5045EX-4R7M
R1: 10k; R_0603_HandSoldering
R2: 2.2k; R_0603_HandSoldering
R3: 8.2Ω 3W; R_Axial_Power_L25.0mm_W6.4mm_P27.94mm
R4: 8.2Ω 3W; R_Axial_DIN0617_L17.0mm_D6.0mm_P20.32mm_Horizontal
R5, R6, R7, R8, R9: 1k?W; R_2512_HandSoldering
R10: 220k; R_0603_HandSoldering
R11: 0; R_0603_HandSoldering
R12: 39k; R_0603_HandSoldering
U1, U2, U3, U4, U5: TL431PK; NJM431U-ND
U6: BD9D320EFJ-E2; SOIC-8-1EP_3.9x4.9mm_Pitch1.27mm

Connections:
5V: C15.1, C16.1, C17.1, J9.2, J9.4, L1.2, R10.1
12V_BD_VIN: C1.1, C2.1, C3.1, C4.1, C5.1, C11.1, F1.1, J3.1, J8.1, U6.1, U6.8
/BD_BOOT: C14.1, U6.7
/BD_FB: C15.2, R11.2, R12.1, U6.2
/BD_SW: C14.2, L1.1, U6.6
GND: C1.2, C2.2, C3.2, C4.2, C5.2, C10.2, C11.2, C12.2, C13.2, C16.2, C17.2, D1.2, J1.2, J1.3, J2.2, J3.2, J9.6, J9.9, J9.14, J9.20, J9.25, J9.30, J9.34, J9.39, R2.2, R9.1, R12.2, U5.2, U5.2.1, U6.5, U6.9
unnamed: C6.1, D3.2, J6.1, R3.1, R4.1, U1.1, U1.3
unnamed: C6.2, C7.1, R5.2, R6.2, U1.2, U1.2.1, U2.1, U2.3
unnamed: C7.2, C8.1, R6.1, R7.2, U2.2, U2.2.1, U3.1, U3.3
unnamed: C8.2, C9.1, R7.1, R8.2, U3.2, U3.2.1, U4.1, U4.3
unnamed: C9.2, C10.1, R8.1, R9.2, U4.2, U4.2.1, U5.1, U5.3
unnamed: C12.1, U6.4
unnamed: C13.1, U6.3
unnamed: D2.1, J4.1
unnamed: D3.1, J4.2, J7.1, JP1.2
unnamed: F1.2, J7.2, J8.2
unnamed: J6.2, R5.1
unnamed: JP1.1, R4.2
unnamed: JP1.3, R3.2
unnamed: R10.2, R11.1
VIN: D1.1, D2.2, J1.1, J2.1, R1.1
VIN_SENSE: J9.33, R1.2, R2.1

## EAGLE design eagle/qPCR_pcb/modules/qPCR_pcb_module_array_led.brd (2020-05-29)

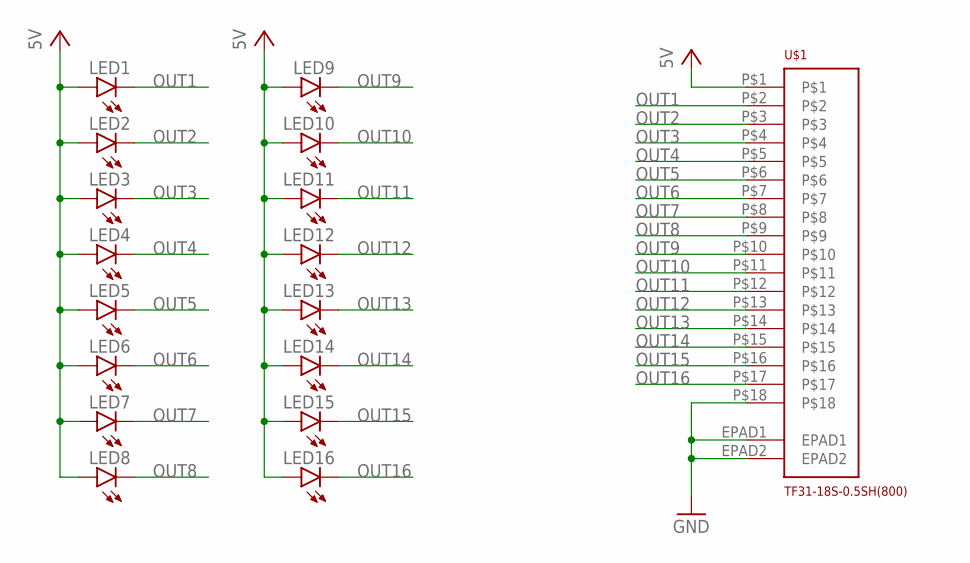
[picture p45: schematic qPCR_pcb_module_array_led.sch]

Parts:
LED1, LED2, LED3, LED4, LED5, LED6, LED7, LED8, LED9, LED10, LED11, LED12, LED13, LED14, LED15, LED16: LED5MM
U$1: TF31-18S-0.5SH(800)

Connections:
5V: LED1.A, LED2.A, LED3.A, LED4.A, LED5.A, LED6.A, LED7.A, LED8.A, LED9.A, LED10.A, LED11.A, LED12.A, LED13.A, LED14.A, LED15.A, LED16.A, U$1.P$1
GND: U$1.EPAD1, U$1.EPAD2, U$1.P$18
OUT1: LED1.K (C), U$1.P$2
OUT2: LED2.K (C), U$1.P$3
OUT3: LED3.K (C), U$1.P$4
OUT4: LED4.K (C), U$1.P$5
OUT5: LED5.K (C), U$1.P$6
OUT6: LED6.K (C), U$1.P$7
OUT7: LED7.K (C), U$1.P$8
OUT8: LED8.K (C), U$1.P$9
OUT9: LED9.K (C), U$1.P$10
OUT10: LED10.K (C), U$1.P$11
OUT11: LED11.K (C), U$1.P$12
OUT12: LED12.K (C), U$1.P$13
OUT13: LED13.K (C), U$1.P$14
OUT14: LED14.K (C), U$1.P$15
OUT15: LED15.K (C), U$1.P$16
OUT16: LED16.K (C), U$1.P$17

Board: 2 copper layers, 17 parts (0 on the bottom side), 18 nets, no tracks yet.

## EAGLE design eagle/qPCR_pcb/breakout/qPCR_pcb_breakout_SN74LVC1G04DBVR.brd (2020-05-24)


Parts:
JP1, JP2, JP3, JP4: PINHD-1X5R; 1X05R
U1: SN74LVC1G04DBVR; DBV5

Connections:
1: JP2.1, U1.1 (NC)
2: JP1.1, U1.2 (A)
3: JP2.2, U1.3 (GND)
4: JP1.2
5: JP2.3
6: JP1.3
7: JP2.4
8: JP1.4
9: JP2.5
10: JP1.5
11: JP4.5
12: JP3.5
13: JP4.4
14: JP3.4
15: JP4.3
16: JP3.3
17: JP4.2
18: JP3.2, U1.4 (Y)
19: JP4.1
20: JP3.1, U1.5 (VCC)



Board: 2 copper layers, 35.6 x 15.2 mm, 5 parts (4 on the bottom side), 5 nets.

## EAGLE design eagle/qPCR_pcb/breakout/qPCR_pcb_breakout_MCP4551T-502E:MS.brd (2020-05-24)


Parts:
JP1, JP3: PINHD-1X4; 1X04
U1: MCP4551T-502E/MS; MSOP8_MC_MCH

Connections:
1: JP1.1, U1.1 (HVC/A0)
2: JP1.2, U1.2 (SCL)
3: JP1.3, U1.3 (SDA)
4: JP1.4, U1.4 (VSS)
5: JP3.4, U1.5 (P0A)
6: JP3.3, U1.6 (P0W)
7: JP3.2, U1.7 (P0B)
8: JP3.1, U1.8 (VDD)



Board: 2 copper layers, 17.8 x 12.7 mm, 3 parts (2 on the bottom side), 8 nets.

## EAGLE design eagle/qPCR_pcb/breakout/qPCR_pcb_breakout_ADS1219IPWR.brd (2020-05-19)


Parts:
JP1, JP2: PINHD-1X8; 1X08
U1: Value; PW0016A_N

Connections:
1: JP1.1, U1.1 (A0)
2: JP1.2, U1.2 (A1)
3: JP1.3, U1.3 (RESET_N)
4: JP1.4, U1.4 (DGND)
5: JP1.5, U1.5 (AVSS)
6: JP1.6, U1.6 (AIN3)
7: JP1.7, U1.7 (AIN2)
8: JP1.8, U1.8 (REFN)
9: JP2.8, U1.9 (REFP)
10: JP2.7, U1.10 (AIN1)
11: JP2.6, U1.11 (AIN0)
12: JP2.5, U1.12 (AVDD)
13: JP2.4, U1.13 (DVDD)
14: JP2.3, U1.14 (DRDY_N)
15: JP2.2, U1.15 (SDA)
16: JP2.1, U1.16 (SCL)



Board: 2 copper layers, 20.3 x 22.9 mm, 3 parts (2 on the bottom side), 16 nets.

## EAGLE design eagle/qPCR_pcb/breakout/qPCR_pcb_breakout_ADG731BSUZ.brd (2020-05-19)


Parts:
JP1, JP2: PINHD-1X24; 1X24
U1: ADG731BSUZ; SU_48_ADI

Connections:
1: JP1.1, U1.1 (S12)
2: JP1.2, U1.2 (S11)
3: JP1.3, U1.3 (S10)
4: JP1.4, U1.4 (S9)
5: JP1.5, U1.5 (S8)
6: JP1.6, U1.6 (S7)
7: JP1.7, U1.7 (S6)
8: JP1.8, U1.8 (S5)
9: JP1.9, U1.9 (S4)
10: JP1.10, U1.10 (S3)
11: JP1.11, U1.11 (S2)
12: JP1.12, U1.12 (S1)
13: JP1.13, U1.13 (VDD_2)
14: JP1.14, U1.14 (VDD)
15: JP1.15, U1.15 (NC_2)
16: JP1.16, U1.16 (NC_3)
17: JP1.17, U1.17 (SYNC)
18: JP1.18, U1.18 (DIN)
19: JP1.19, U1.19 (SCLK)
20: JP1.20, U1.20 (NC_4)
21: JP1.21, U1.21 (NC_5)
22: JP1.22, U1.22 (NC_6)
23: JP1.23, U1.23 (GND)
24: JP1.24, U1.24 (VSS)
25: JP2.24, U1.25 (S17)
26: JP2.23, U1.26 (S18)
27: JP2.22, U1.27 (S19)
28: JP2.21, U1.28 (S20)
29: JP2.20, U1.29 (S21)
30: JP2.19, U1.30 (S22)
31: JP2.18, U1.31 (S23)
32: JP2.17, U1.32 (S24)
33: JP2.16, U1.33 (S25)
34: JP2.15, U1.34 (S26)
35: JP2.14, U1.35 (S27)
36: JP2.13, U1.36 (S28)
37: JP2.12, U1.37 (S29)
38: JP2.11, U1.38 (S30)
39: JP2.10, U1.39 (S31)
40: JP2.9, U1.40 (S32)
41: JP2.8, U1.41 (NC_7)
42: JP2.7, U1.42 (NC_8)
43: JP2.6, U1.43 (D)
44: JP2.5, U1.44 (NC)
45: JP2.4, U1.45 (S16)
46: JP2.3, U1.46 (S15)
47: JP2.2, U1.47 (S14)
48: JP2.1, U1.48 (S13)



Board: 2 copper layers, 27.9 x 63.5 mm, 3 parts (2 on the bottom side), 48 nets.

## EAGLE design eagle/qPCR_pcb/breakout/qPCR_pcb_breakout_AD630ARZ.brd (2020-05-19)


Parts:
JP3, JP4: PINHD-1X10; 1X10
U1: AD630ARZ; RW_20_ADI

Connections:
1: JP3.1, U1.1 (RINA)
2: JP3.2, U1.2 (CH_A+)
3: JP3.3, U1.3 (DIFF_OFF_ADJ)
4: JP3.4, U1.4 (DIFF_OFF_ADJ_2)
5: JP3.5, U1.5 (CM_OFF_ADJ)
6: JP3.6, U1.6 (CM_OFF_ADJ_2)
7: JP3.7, U1.7 (!)
8: JP3.8, U1.8 (-VS)
9: JP3.9, U1.9 (SEL_B)
10: JP3.10, U1.10 (SEL_A)
11: JP4.10, U1.11 (+VS)
12: JP4.9, U1.12 (COMP)
13: JP4.8, U1.13 (VOUT)
14: JP4.7, U1.14 (RB)
15: JP4.6, U1.15 (RF)
16: JP4.5, U1.16 (RA)
17: JP4.4, U1.17 (RINB)
18: JP4.3, U1.18 (CH_B+)
19: JP4.2, U1.19 (CH_B-)
20: JP4.1, U1.20 (CH_A-)



Board: 2 copper layers, 22.9 x 27.9 mm, 3 parts (2 on the bottom side), 20 nets.

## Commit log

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2020-05-06 initialize pcb
    [qPCR_pcb_led_ver1.0.brd, qPCR_pcb_led_ver1.0.sch, qPCR_pcb_main_ver1.0.brd, qPCR_pcb_main_ver1.0.sch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]
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2020-05-17 add sandbox
    [qPCR_pcb_module_sense.sch]
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2020-05-19 add breakouts
    [qPCR_pcb_breakout_AD630ARZ.brd, qPCR_pcb_breakout_AD630ARZ.sch, qPCR_pcb_breakout_ADG731BSUZ.brd, qPCR_pcb_breakout_ADG731BSUZ.sch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]
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2020-05-24 add female headers
    [hf_1x1.step, hf_1x10.step, hf_1x11.step, hf_1x12.step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]
2020-05-24 correct footprint
    [qPCR_pcb_breakout_SN74LVC1G04DBVR.brd, qPCR_pcb_breakout_SN74LVC1G04DBVR.sch, qPCR_pcb_module_sense.sch]
2020-05-29 add kicad
    [Ninja-qPCR.sch, qPCR-ledarray.kicad_pcb, qPCR-ledarray.sch, qPCR-ledarray.step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]
2020-05-30 add slide0
    [qPCR-photoarray.kicad_pcb]
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2020-07-20 add diagram
    [Ninja-qPCR.sch, bench_ver1.0.kicad_pcb, bench_ver1.0.sch, qPCR-ledarray.kicad_pcb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]
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2020-08-07 ordered 1st batch of PCBs to Seeed
    [Ninja-qPCR.sch, breakout_2x5-B_Cu.gbl, breakout_2x5-B_Mask.gbs, breakout_2x5-B_Paste.gbp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]
2020-08-12 sync ver1.1
    [1x8_board_back.dxf, 1x8_board_bottom.dxf, 1x8_board_con_body.dxf, 1x8_board_front.dxf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]
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2020-08-25 ordered batch1
    [1x8_board_lid.dxf, 2x8_board_lid.dxf, breakout_2x5-B_Cu.gbl, breakout_2x5-B_Mask.gbs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]
2020-08-26 Add ledcontrol board to KiCad project
    [qPCR-ledcontrol.sch]
2020-08-26 Add LED control board
    [qPCR-ledcontrol.sch]
2020-08-26 Add photosensing board
    [qPCR-photosensing.sch]
2020-08-26 Add photosensing circuit
    [qPCR-photosensing.sch]
2020-08-27 Add Lid-body & main boards
    [qPCR-lid_body.sch, qPCR-main.sch]
2020-09-01 Add schematics
    [qPCR-ledcontrol.sch, qPCR-lid_body.sch, qPCR-main.sch, qPCR-main_power_input.sch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]
2020-09-01 Add photosensing boards
    [qPCR-photosensing_amp.sch]
2020-09-01 Add led array schematics
    [qPCR-ledarray.sch]
2020-09-02 minor corrections
    [qPCR-ledcontrol.sch]
2020-09-08 add schematics of test boards
    [con_body.kicad_pcb, con_body.sch, con_lid_1x8.kicad_pcb, con_lid_1x8.sch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]
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2020-09-10 wire photosensing
    [qPCR-photosensing-B_Cu.gbl, qPCR-photosensing-B_Mask.gbs, qPCR-photosensing-B_Paste.gbp, qPCR-photosensing-B_SilkS.gbo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]
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2020-09-15 add LTC
    [fileSPI.sch, qPCR-main.sch, qPCR-photosensing-B_Cu.gbl, qPCR-photosensing-B_Mask.gbs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]
2020-09-15 main schematic finished
    [filePower.sch, fileSPI.sch, qPCR-main.sch]
2020-09-16 wiring main
    [fileSPI.sch, qPCR-main.kicad_pcb, qPCR-main.sch]
2020-09-18 main wired
    [filePower.sch, fileSPI.sch, qPCR-main.kicad_pcb, qPCR-main.sch]
2020-09-19 ordered batch2
    [qPCR-main-B_Cu.gbl, qPCR-main-B_Mask.gbs, qPCR-main-B_Paste.gbp, qPCR-main-B_SilkS.gbo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]
2020-09-23 relocate silk
    [qPCR-ledarray.sch, qPCR-ledcontrol-BOM.csv, qPCR-ledcontrol.kicad_pcb, qPCR-main-BOM.csv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]
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2020-10-07 add batch3
    [qPCR-main.kicad_pcb]
2020-10-08 add batch3/photosensing
    [qPCR-photosensing.sch]
2020-12-17 Add XTAL test circuit
    [qPCR-xtal.sch]
2020-12-17 Add batch3 photosensing circuit
    [fileConnector.sch, fileLidBody.sch, filePower.sch, fileSPI.sch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]
2020-12-18 Photosensing board
    [qPCR-main.sch, qPCR-photosensing.sch, qPCR-xtal.sch]
2020-12-19 Add comments to X'tal circuit
    [qPCR-photosensing.sch]
2020-12-22 Change label property
    [qPCR-photosensing.sch]
2020-12-22 Add gain switching to the pre-amp
    [qPCR-photosensing.sch]
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2021-01-04 add greengrass
    [greengrass-B_Cu.gbl, greengrass-B_Mask.gbs, greengrass-B_Paste.gbp, greengrass-B_SilkS.gbo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]
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2021-01-05 add batch3/gg. remove batch3/main
    [fileConnector.sch, fileLidBody.sch, filePower.sch, fileSPI.sch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]
2021-01-06 wire xtal
    [qPCR-photosensing.sch, qPCR-xtal-B_Cu.gbl, qPCR-xtal-B_Mask.gbs, qPCR-xtal-B_Paste.gbp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]
2021-01-06 Filled values of X'tal circuit
    [qPCR-xtal.sch]
2021-01-06 change 20M to 10M+10M
    [qPCR-photosensing.sch, qPCR-xtal-B_Cu.gbl, qPCR-xtal-B_Mask.gbs, qPCR-xtal-B_Paste.gbp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]
2021-01-06 Updated values of resistor & capacitors of photosensing board
    [qPCR-photosensing.sch]
2021-01-07 initialize batch4/main
    [fileConnector.sch, fileLidBody.sch, filePower.sch, fileSPI.sch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]
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2021-01-14 add batch4/photoarray-series
    [qPCR-photoarray-series-B_Cu.gbl, qPCR-photoarray-series-B_Mask.gbs, qPCR-photoarray-series-B_Paste.gbp, qPCR-photoarray-series-B_SilkS.gbo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]
2021-01-27 add workflow
    [qPCR-main.sch, qPCR-photoarray-series.sch, qPCR-photosensing.kicad_pcb, qPCR-xtal.kicad_pcb]
2021-02-02 Add analysis stub
    [qPCR-photosensing.kicad_pcb]
2021-02-05 add todo message to pull-up
    [qPCR-photosensing.sch]
2021-02-08 Updated photosensing circuit for batch4
    * Add pull-up resistors to SPI wires
    * Add reset circuit to RST
    [qPCR-photosensing.sch]
2021-02-15 connect floating VCC_LOGIC to 3V3_RASP
    [filePower.sch, qPCR-main.sch]
2021-02-16 buildup batch4/main
    [fileLEDCtrl.sch, filePhotoSensing.sch, filePower.sch, qPCR-main.sch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]
2021-02-17 Support MUX
    [qPCR-photo_mux_ADG706BRUZ-ND.kicad_pcb, qPCR-photosensing.kicad_pcb]
2021-02-17 use SPDT switch for SPI MOSI
    [qPCR-main.sch]
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2021-02-19 add gg component yaml
    [fileLEDCtrl.sch, filePhotoSensing.sch, filePower.sch, filePowerRasp.sch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]
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2021-03-02 supercap sch done
    [qPCR-photo_mux_74HC4067SSOP-B_Cu.gbl, qPCR-photo_mux_74HC4067SSOP-B_Mask.gbs, qPCR-photo_mux_74HC4067SSOP-B_Paste.gbp, qPCR-photo_mux_74HC4067SSOP-B_SilkS.gbo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]
2021-03-02 batch4 ordered
    [qPCR-supercap-B_Cu.gbl, qPCR-supercap-B_Mask.gbs, qPCR-supercap-B_Paste.gbp, qPCR-supercap-B_SilkS.gbo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]
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2021-04-02 Add batch6 schematics
    [qPCR-photo_mux_74HC4067SSOP.kicad_pcb, qPCR-photo_mux_74HC4067SSOP.sch, qPCR-photosensing.kicad_pcb, qPCR-photosensing.sch]
2021-04-05 use proper lib
    [qPCR-photosensing.sch]
2021-04-05 Add symbols to KiCad lib / Batch6 photosensing sch.
    [qPCR-photosensing.sch]
2021-04-06 Photosensing batch6
    [qPCR-photosensing.sch]
2021-04-06 Add library/Edit mux & photosensing boards
    [qPCR-photo_mux_74HC4067SSOP.sch, qPCR-photosensing.sch]
2021-04-07 Add debug pads / oscillator jumper
    [qPCR-photosensing.sch]
2021-04-14 Add comment
    [qPCR-photosensing.sch]
2021-04-14 Update photosensing circuit
    * Add reset circuit (10uF capacitor)
    * Add comments
    [qPCR-photosensing.sch]
2021-04-14 use 1x05 pinhead
    [qPCR-photo_mux_74HC4067SSOP.sch, qPCR-photosensing.sch]
2021-04-14 photo_mux done
    [qPCR-photo_mux_74HC4067SSOP-B_Cu.gbl, qPCR-photo_mux_74HC4067SSOP-B_Mask.gbs, qPCR-photo_mux_74HC4067SSOP-B_Paste.gbp, qPCR-photo_mux_74HC4067SSOP-B_SilkS.gbo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]
2021-04-14 just before cleaning up
    [qPCR-photosensing.sch]
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2021-04-27 Connect Amp's VSS to negative bias line
    [qPCR-photosensing.sch]
2021-05-07 add pushpin
    [qPCR-panel_20210427.kicad_pcb]
2021-05-17 set note
    [qPCR-main.sch]
2021-05-27 Add batch8 Photosensing and Main
    [batch2_main.sch, con_body.sch, con_lid_2x8.sch, fileLED.sch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]
2021-05-27 Add Batch 8 hardware control / Connect RPi 3V3
    [qPCR-main.sch]
2021-06-01 add supercap to main
    [fileSupercap.sch, qPCR-supercap.sch]
2021-06-01 add pi footprints
    [qPCR-main.kicad_pcb, qPCR-main.sch]
2021-06-01 add con1x4 for rpi lcd
    [qPCR-main.sch]
2021-06-01 remove con1x4 for rpi lcd
    [qPCR-main.sch]
2021-06-03 abstract layout
    [fileLED.sch, filePower.sch, fileSupercap.sch, fileThermistors.sch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]
2021-06-03 flip properly
    [qPCR-main.kicad_pcb]
2021-06-03 move components
    [qPCR-main.kicad_pcb]
2021-06-03 Add tact switch / Replace thermistor MUX
    [fileThermistors.sch, qPCR-main.sch]
2021-06-04 Add door sensor & latch circuit
    [qPCR-main.sch]
2021-06-04 remove unnecessary R
    [qPCR-main.sch]
2021-06-04 remove cheapest LCD and tacts
    [filePower.sch, fileSupercap.sch, fileThermistors.sch, qPCR-main.kicad_pcb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]
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2021-06-10 Replace ADC
    [qPCR-photosensing.sch]
2021-06-10 Replace gain switch, OpAmp, MUX and ADC
    [filePhotoNorth.sch, filePhotoSouth.sch, qPCR-photosensing.sch]
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2021-06-11 replace parts with enough stock
    [fileLED.sch, filePhotoSouth.sch, filePower.sch, fileSupercap.sch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]
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2021-06-17 Replace connector on root board
    [qPCR-root.kicad_pcb]
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2021-06-20 Update photosensing board / replace thermistor connectors
    [fileThermistors.sch, qPCR-photosensing.kicad_pcb]
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2021-08-31 correct led
    [photo-single-B_Cu.gbl, photo-single-B_Mask.gbs, photo-single-B_Paste.gbp, photo-single-B_SilkS.gbo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]
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2021-09-24 replace parts in stock
    [file12V_UPS.sch, qPCR-main.kicad_pcb]
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2021-10-25 fix global/local problem
    [file-1V.sch, file12V_UPS.sch, file3V3.sch, file5V_UPS.sch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]
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2021-12-07 fixed optic hold system
    [photo-dual-B_Cu.gbl, photo-dual-B_Mask.gbs, photo-dual-B_Paste.gbp, photo-dual-B_SilkS.gbo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]
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2022-01-27 minor fixes onto batch18/main
    [5VUPS.kicad_sch, file-1V.kicad_sch, file12V_UPS.kicad_sch, file3V3.kicad_sch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]
2022-02-16 replace chips
    [file-1V.kicad_sch, file12V_UPS.kicad_sch, file3V3.kicad_sch, file5V_UPS.kicad_sch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]
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2022-12-02 bugfix paths
    [photo-dual.kicad_pcb, photo-single.kicad_pcb, stepper.kicad_pcb, stepper.kicad_sch]
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

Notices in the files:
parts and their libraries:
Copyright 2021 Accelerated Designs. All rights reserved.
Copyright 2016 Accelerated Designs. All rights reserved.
